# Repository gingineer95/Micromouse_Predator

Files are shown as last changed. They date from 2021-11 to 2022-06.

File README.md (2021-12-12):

Kailey Smith
# Mircomouse Predator from Scratch

## Project Overview

The goal of this project was to design, construct, and control a small wheeled robot, completely from scratch. Dr. Malcolm MacIver’s lab is studying robot-rodent interactions and required a robot to act as a high-speed predator that will constantly try to discover, chase, and corner a mouse in a maze-like habitat. 

To achieve this, I drew knowledge from my previous mechatronics experience to build a motor control circuit, communicate wirelessly using a Digi XBee module radio, as well as create a custom PCB. I also took inspiration from the <a href="https://en.wikipedia.org/wiki/Micromouse" target="_blank" rel="noopener noreferrer">Half-Sized Micromouse Competition</a> for both mechanical and electrical design. 

**The end result:** a remote controlled differential drive robot. Below is a video of robot being given left and right DC commands. It shows the robot moving forward and backwards, turning in a circle, and lastly moving in a loop. Note: these are only feed-forward commands, feed-back control is needed for precise movement.

Please checkout my [portfolio post](https://gingineer95.github.io/2021/12/11/micromouse/) for more details. 

forward_back

## Repo Hierarchy
MPLAB: Contains all C code, including programs used during breadboard testing and PCB testing.

Micromouse_solidworks_assembly: 3D modeled parts and assemblies.

Motor_Analysis: Contains a jupyter notebook in which I analyized different motors to use for the robot.

PCB_design: Contains all Eagle files, including libraries used and schematics/board desings

## Motor Analysis

My goal was to create a simulated “race” between a given brushed DC motor and the mice to find motors that ran faster than the mice. Dr. MaIver’s lab provided me with mouse trajectory and velocity data over time from their ongoing experiments. With this information to compare to, I needed to extrapolate equations to calculate a motor’s position and linear velocity over time given only a motor’s electrical specs. 

To model the motor’s behavior, I started using a simple equation that expresses input and outputs in terms of power below:

<p align="center">
\large {\color{White} IV = \tau \omega + {I}^2 R}   
</p>

Where *I* is the current through the motor, *V* is the voltage across the motor, \large {\color{White} \tau} and \large {\color{White} \omega} stand for torque and angular velocity on the output shaft and R is the motor’s internal resistance. The left side of the equation accounts for the electrical input power into a motor, while the right side accounts for the mechanical output power and power expelled through heat dissipation. After substituting in the torque constant {\color{White} k_t = \tau / I}, then {\color{White} \tau = mar} for torque, and {\color{White} \omega = v / r} for omega, I solved for an equation that is represented by the 1st and 2nd and 1st order differentials of displacement over time:

<p align="center">
\large {\color{White} a + \frac{v {k_t}^2}{Rm{r}^2} - \frac{V k_t}{Rmr} = 0} 
</p>

<p align="center">
\large {\color{White} \frac{d^2 x}{dt^2} + \frac{dx {k_t}^2}{Rm{r}^2 dt} - \frac{V k_t}{Rmr} = 0}
</p>

Once I had a function that was dependent on displacement over time, I was able to run the “race” simualtions. In order to get the robots linear and velocity displacement over time to compare to they mice, solved the equation for *x(t)* as well as *x'(t)*:

<p align="center">
\large {\color{White} x(t) = \frac{rV(k_t^2G^2 t + Rm{r}^2 ({e}^{-\frac{k_t^2G^2 t}{Rm{r}^2}} - 1))}{k_t^3G^3}}
</p>
<p align="center">
\large {\color{White} x'(t) = \frac{rV}{k_tG} (1 - {e}^{-\frac{k_t^2G^2 t}{Rm{r}^2}})}
</p>

Using the equations, I compared several motors to the mice by creating graphs such as the two below. The blue line represents the motor’s data while the green line represents a mouse.

mouse_race_data

I also examined each motor’s torque-speed curve to ensure that a motor’s anticipated torque outputs were within the continuous operating region of that motor. Using all graphs I was able to eliminate several motors while still having a couple of viable motors to choose from. 

My final motor selection came down to weight and size. For this entire system, the motors and battery we’re the largest and heaviest components. Therefore I wanted the smallest and lightest option of both. This meant choosing a 1 cell battery and therefore a motor that only needed up to 3.7V to operate. After doing some initial mechanical modeling, I chose a light and small motor that fit the design configuration I was looking for. 

## PCB Design

Once the critical parts were chosen, it was time to order all the other circuit components so I could start breadboarding and testing the circuit before ordering a custom PCB. I chose to use a PIC32 microcontroller since I had previous experience with these chips and there were a couple on hand to get started with quickly. Along those lines, I also chose to use the TI DRV8833 motor drivers. As a safety precaution, I added IR distance sensors to detect objects and avoid collisions. The last key component to this circuit was the Digi XBee 3 802.15.4 module which I used to communicate wirelessly with the robot. 

In order to integrate all the circuit components into a small area on the robot, a custom PCB was necessary. After I confirmed that my circuit worked on the breadboard, I had confidence that I could design a functional PCB. 

My initial thought was to use the PCB as a chassis component, as many of the Micromouse robots do. However, the MacIver lab uses a camera system above their habitat to track the mice and robot. And in order to detect, track, and determine the orientation of the robot, 3 red LEDs need to form an isosceles triangle on top of the robot. Given that, it was simple to rework the mechanical design so the PCB was the top-most component.

As with all PCB prototyping, this was a very iterative process, especially considering how many components needed to fit in such a small space. The dimensions of the PCB were determined by the footprint of the robot, which in turn was driven by the length of the motors. I was able to fit 35 components in a 46cm x 34cm space as pictured below.

<div align="center">View from OSHPark</div>

osh_park

Once the boards were manufactured, I soldered all the individual components myself using a microscope. I quickly realized I couldn’t program my microcontroller. I did a continuity test to identify the issue and discovered I didn’t have common ground across all the components. To get my PCB up and running as quickly as possible, I soldered jumper wires to all components that needed common ground. After that I was able to program the PIC and confirm that all my other connections were correct. I designed a new board with common ground for future use. 

<p align="center">

  board_wXB

</p>

## Mechanical Design

Below are images of the finalized, differential drive robot that I modeled in Soldiworks and then 3D printed.

<div align="center">Final design, 5cm wide by 5.5cm long</div>
<p align="center">

side1

iso1

</p>

I started with a four wheel configuration like many of the Micromouse designs. But after some testing, I discovered that the flooring in the MacIver lab habitat has a much higher coefficient of friction than the flooring used in the Micromouse competitions. I decided to remove two wheels and switch the tire material to a harder rubber o-ring which were skinner and therefore had smaller areas of contact to make turns easier. The thinner wheels also had the benefit of making the overall width of the robot smaller.

<p align="center">

  4wheel

2wheel
</p>

## Next Steps

As a safety feature the next immediate step will be incorporating the IR distance sensors as object avoidance / collision detection. I have already accounted for the sensors in my PCB, so all there is left to do is mount the hardware and implement functionality onto the microchip such that the robot stops if it senses that an object is too close. 

Given that there is a mechanically and electrically sound design, the next control steps are to add a PID controller. The MacIver lab is able to track the robot's location as it moves throughout the habitat. With that information, a position feedback controller can be implemented per the block diagram below. 

<p align="center">

pid_block

</p>

Once the PID controller is squared away, the final step for autonomous navigation will be to create a path planning algotihm. This algorithm will recevice a mouse location and plan a route from the robot's location to the mouse while avoiding all obstacles. With that, the predator robot will be fully operational!
Final Project for MSR program at Northwestern.

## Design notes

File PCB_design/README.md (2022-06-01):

Kailey Smith
# Mircomouse Predator from Scratch

## PCB Design

In this directory, I added my custom built library from EAGLE. There are several iterations of my PCB here, the version I'm currently using on the robot is v4, but this version does not have common ground. In the future, v6 should be used.

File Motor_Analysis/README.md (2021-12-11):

Kailey Smith
# Mircomouse Predator from Scratch

## Motor Analysis in Jupyter Notebook

This folder currently containts all the code I've used throughout this project. I'm in the process of commenting it, so please excuse the mess in the meantime. 

Whats important to note here are the Motor_Simulations_and_Torque-Speed_Graphs and Small_motor_analysis. These files are preactically idenitcal, the main difference being the first analysized several Maxon brand DC motors while the second analyzed small coreless pager motors.

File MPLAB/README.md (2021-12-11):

Kailey Smith
# Mircomouse Predator from Scratch

## C and MPLAB

This folder currently containts all the code I've used throughout this project. I'm in the process of commenting it, so please excuse the mess in the meantime. 

Whats important to note here are the 130_PCB_TEST and 170_PCB_TEST projects made in MPLAB. For this project I had to use two different PICs due to confilcts in my original design and chip availibilty during COVID (PIC32MX**130**F256B and PIC32MX**170**F256B). The functionality of both code is the same, I just had to program the same code twice for the different PICs.

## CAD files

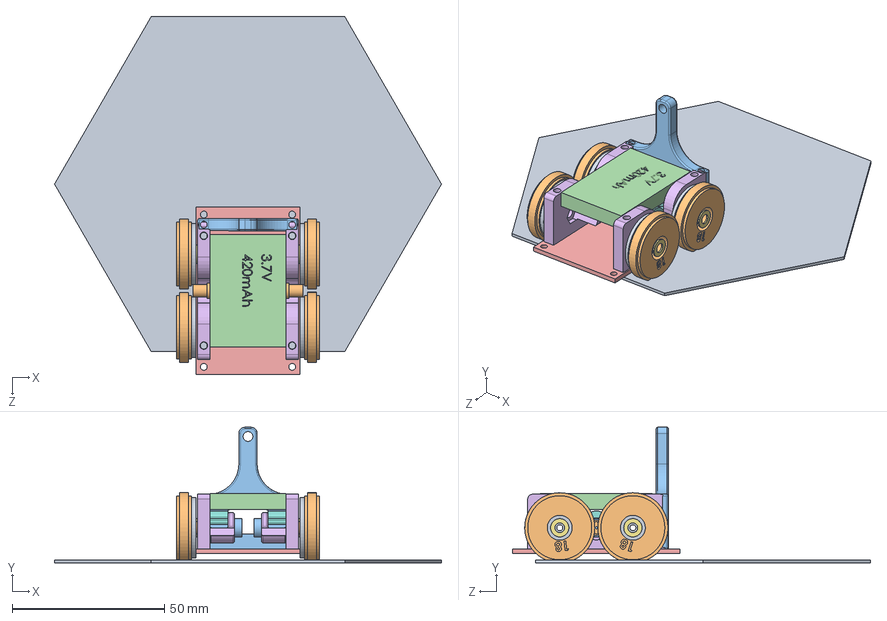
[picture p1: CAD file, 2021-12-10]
Micromouse_solidworks_assembly/MK06-45_assembly.SLDASM
127.0 x 44.5 x 117.5 mm
hex
23OD_wheel_18ID_oring x 4
MK06-45 x 2
37V_420_ada_battery
PCB_v2
motor_mount_bot_v5 x 2
M3_washer x 8
Motor_mount_top x 2
38T2A x 4
8tooth_08A x 2
IR_front_back_mount

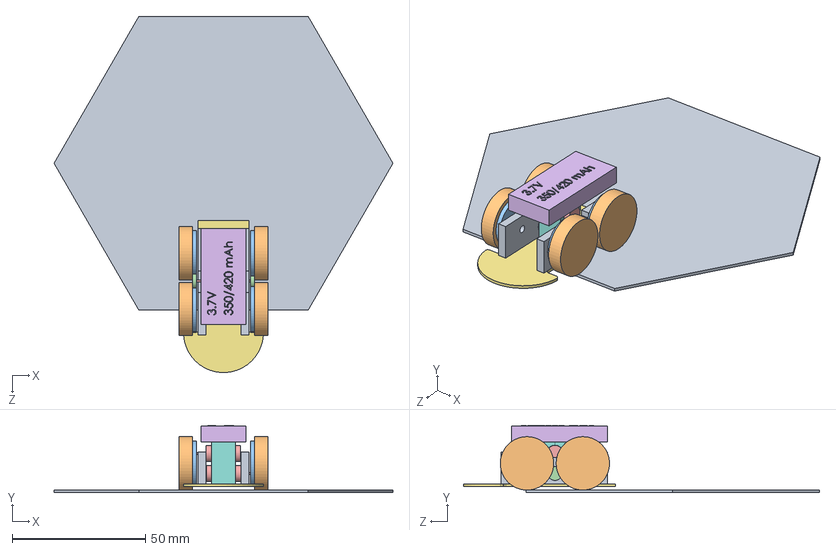
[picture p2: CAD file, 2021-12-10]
Micromouse_solidworks_assembly/MK06-45_stacked_assembly.SLDASM
127.0 x 25.3 x 133.4 mm
hex
2cm_wheel x 4
32tooth_gear_48 x 4
10tooth_gear_48 x 2
MK06-45 x 2
37V_350_420_battery
PCB_MK06_v2
MK06_v2_motor_mount x 2
MK06_v2_wheel_mount x 2

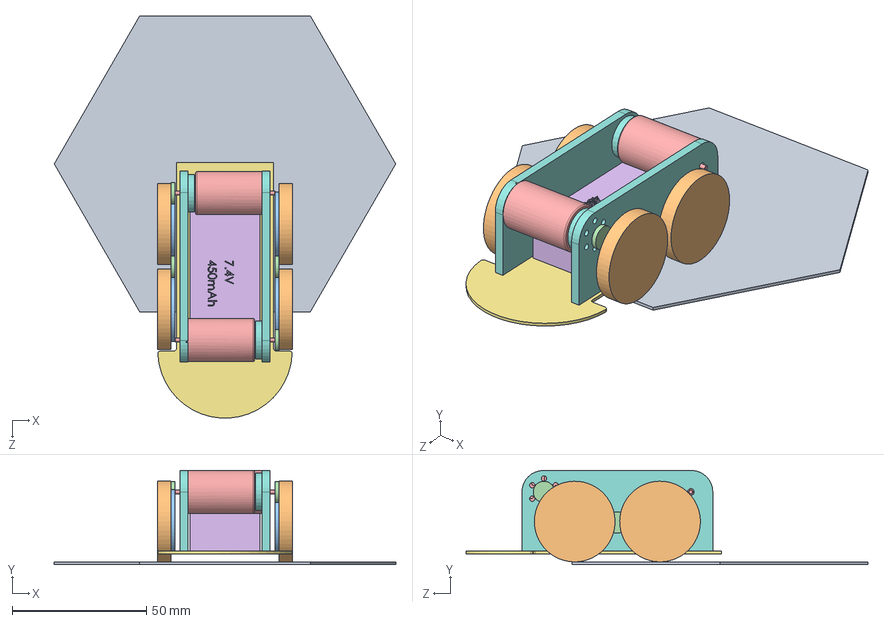
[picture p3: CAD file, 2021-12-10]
Micromouse_solidworks_assembly/DC_max_16S_assembly.SLDASM
127.0 x 35.0 x 149.5 mm
hex
3cm_wheel x 4
30tooth_gear_32 x 4
10tooth_gear_32 x 4
DC_max_16S x 2
7V_450_battery
PCB_16S
16S_motor_mount x 2

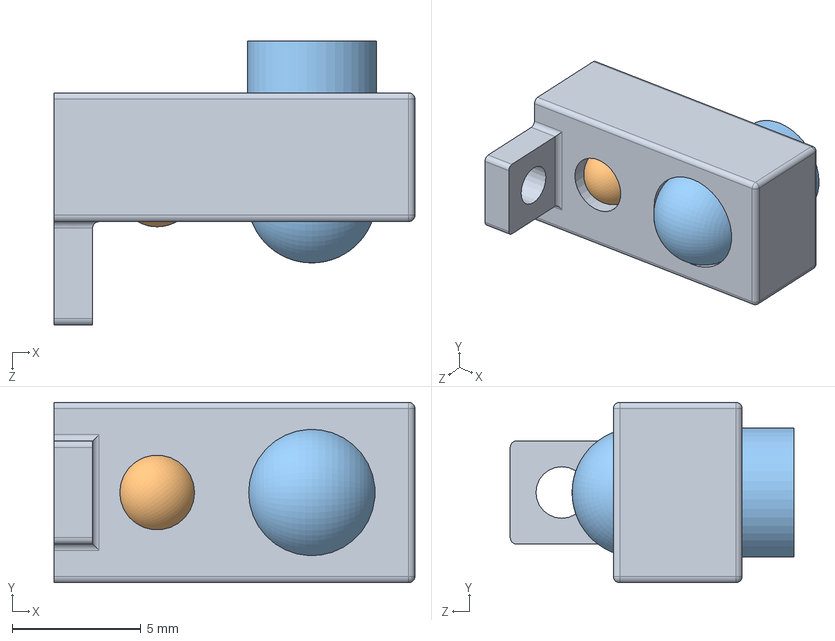
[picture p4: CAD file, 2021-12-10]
Micromouse_solidworks_assembly/IR_combo.SLDASM
14.0 x 7.00 x 11.0 mm
IR_mount
IR_reciver
IR_emmiter

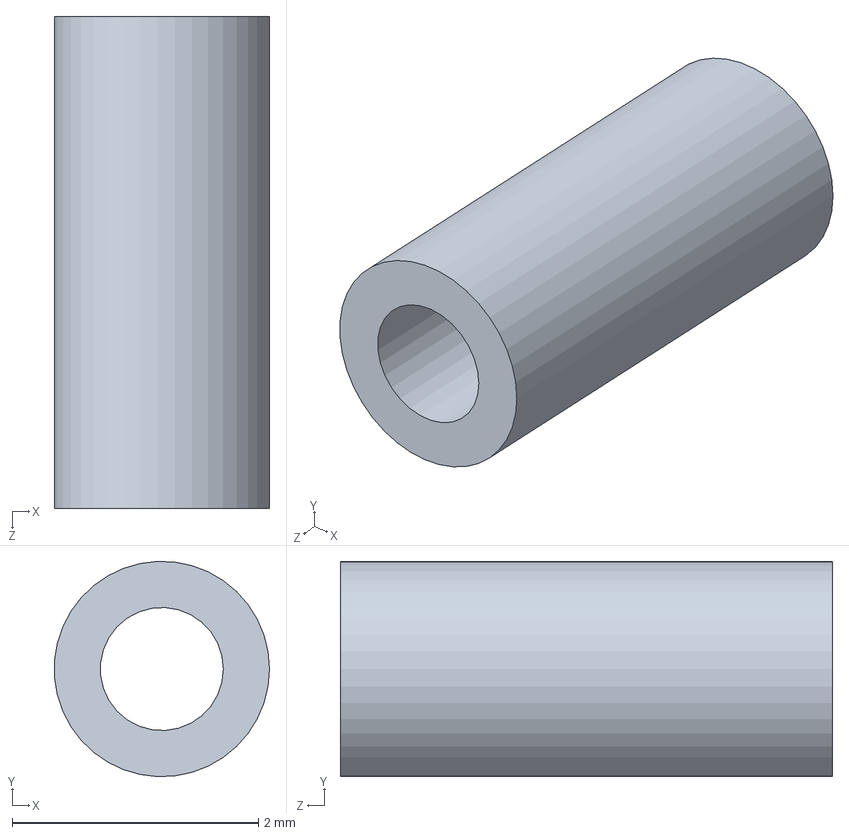
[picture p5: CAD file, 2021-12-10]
Micromouse_solidworks_assembly/1.75mmOD_4mmL_motor_shaft.SLDPRT
1.75 x 1.75 x 4.00 mm

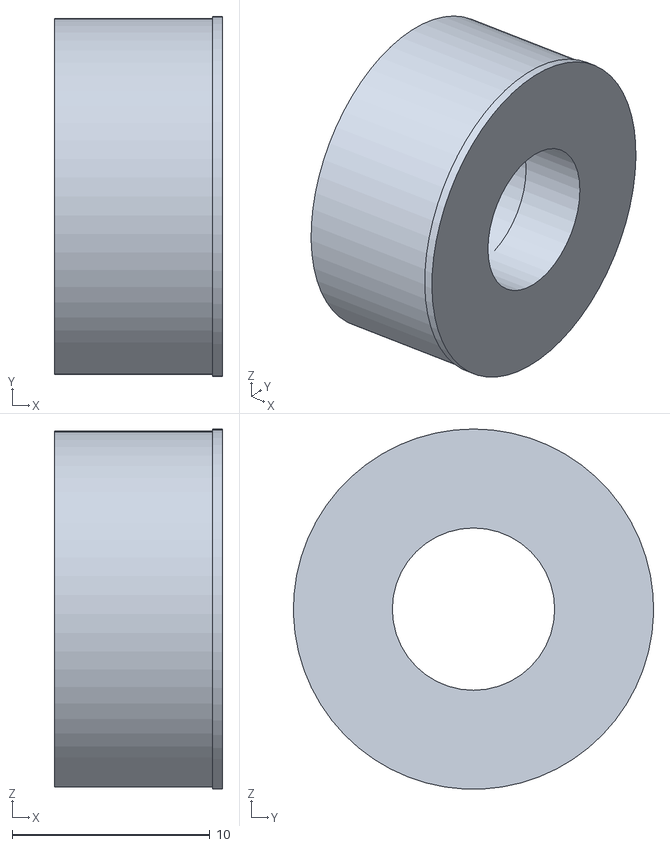
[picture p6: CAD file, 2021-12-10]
Micromouse_solidworks_assembly/STLs/25mm_91_85_kysho_wheel.STL
8.50 x 18.2 x 18.2

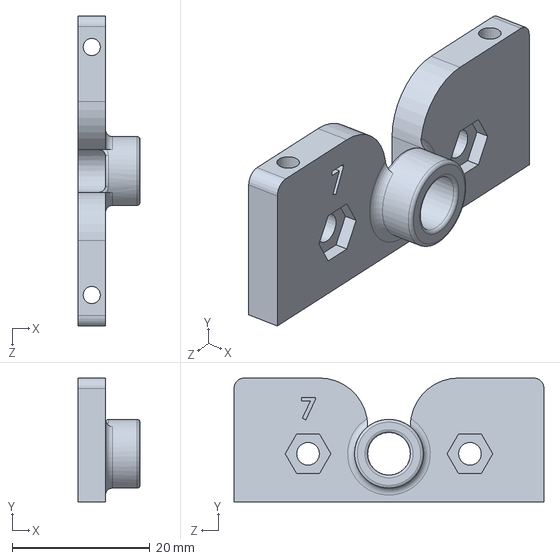
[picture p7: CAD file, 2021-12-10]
Micromouse_solidworks_assembly/motor_mount_bot_v7.SLDPRT
9.00 x 18.0 x 45.0 mm

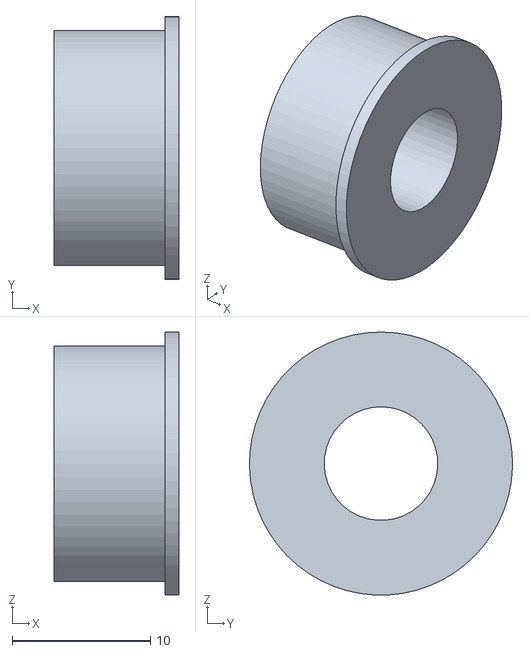
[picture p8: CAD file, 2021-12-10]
Micromouse_solidworks_assembly/STLs/R92mm_9mm_wd_kysho_wheel.STL
9.00 x 19.0 x 19.0

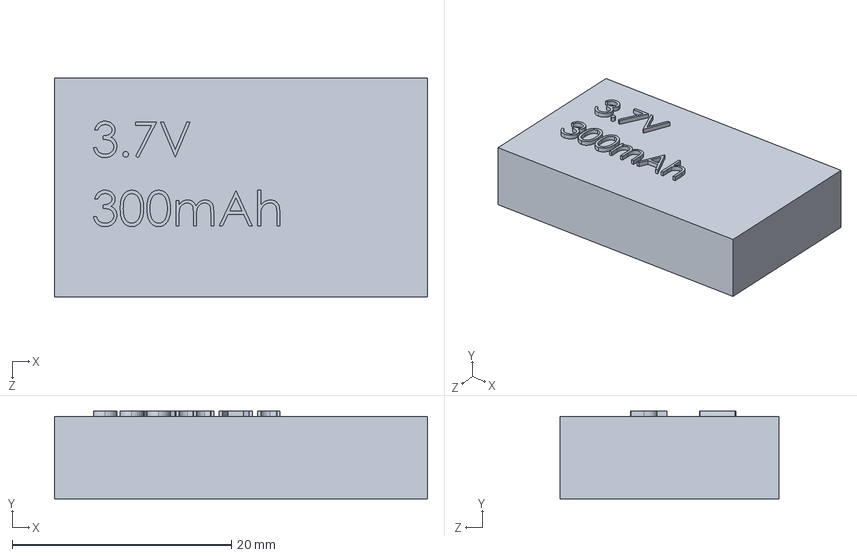
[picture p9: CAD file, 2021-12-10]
Micromouse_solidworks_assembly/37V_300_battery.SLDPRT
34.0 x 8.00 x 20.0 mm

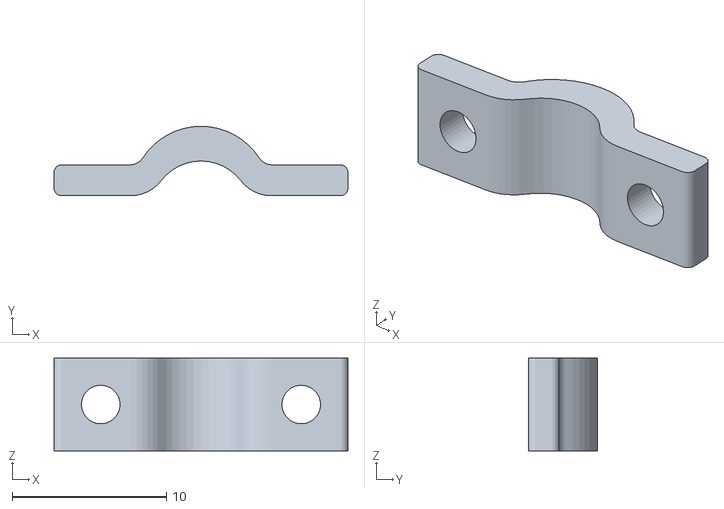
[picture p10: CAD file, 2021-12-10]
Micromouse_solidworks_assembly/STLs/Motor_mount_top_v4.STL
19.1 x 4.50 x 6.00

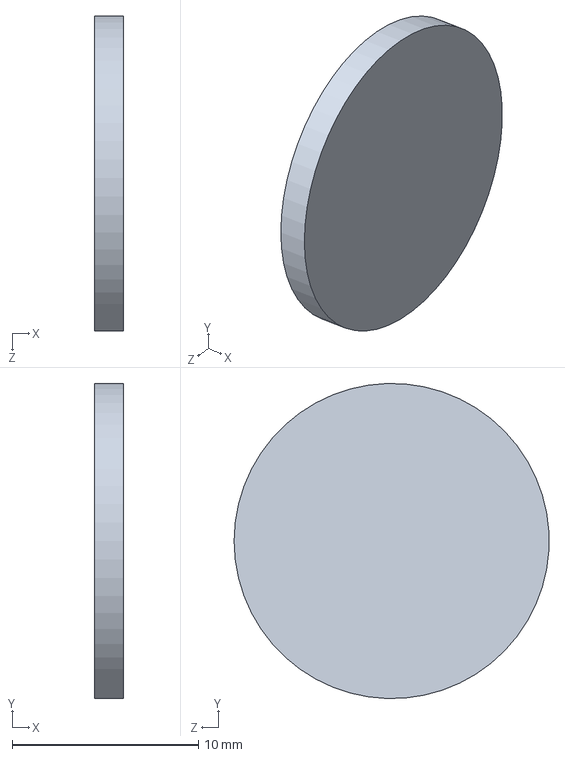
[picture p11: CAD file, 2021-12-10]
Micromouse_solidworks_assembly/32tooth_gear_48.SLDPRT
1.57 x 16.9 x 16.9 mm

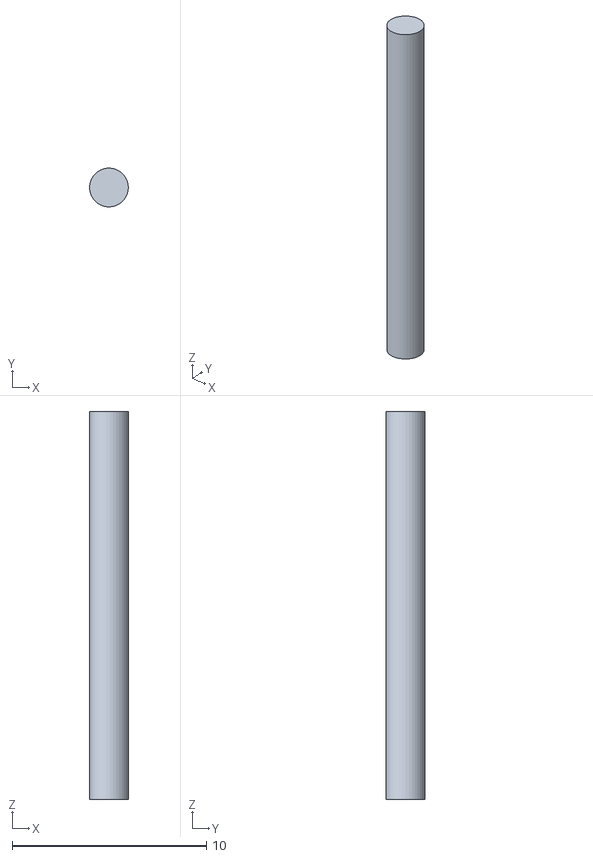
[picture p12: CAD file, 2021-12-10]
Micromouse_solidworks_assembly/STLs/wheel_rod.STL
2.00 x 2.00 x 20.0

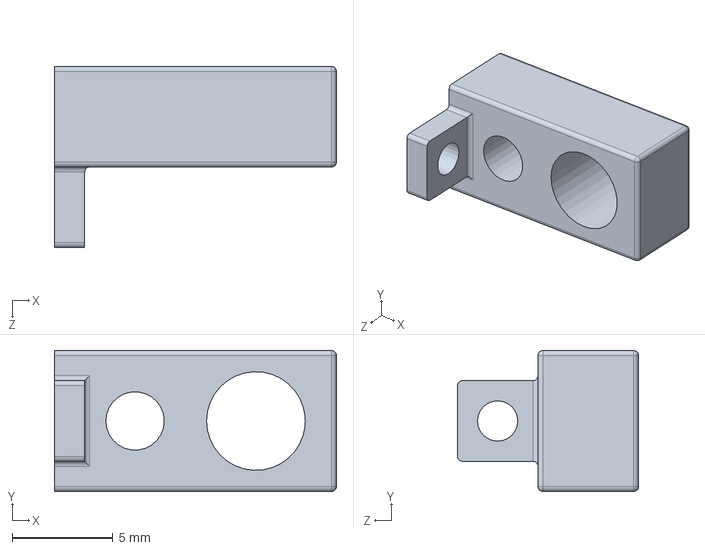
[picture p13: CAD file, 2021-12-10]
Micromouse_solidworks_assembly/IR_mount.SLDPRT
14.0 x 7.00 x 9.00 mm

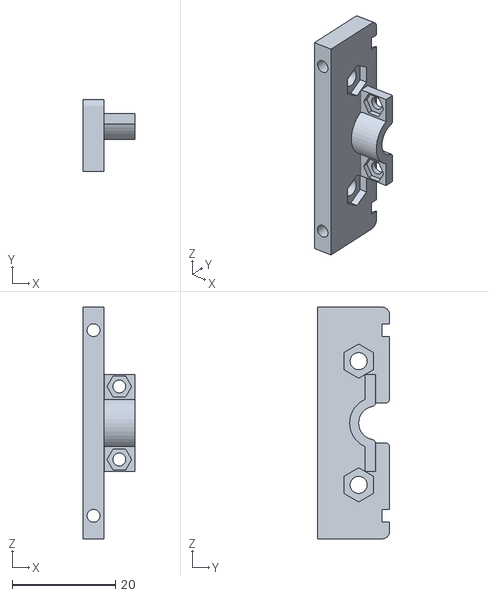
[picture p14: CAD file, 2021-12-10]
Micromouse_solidworks_assembly/STLs/MK06_motor_mount_bottom.STL
10.0 x 14.0 x 45.0

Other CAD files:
Micromouse_solidworks_assembly/PCB_16S.SLDPRT
Micromouse_solidworks_assembly/STLs/PCB_v2_2.STL
Micromouse_solidworks_assembly/hex.SLDPRT
Micromouse_solidworks_assembly/STLs/motor_mount_bot_v3_25cm.STL
Micromouse_solidworks_assembly/10tooth_gear_32.SLDPRT
Micromouse_solidworks_assembly/10tooth_gear_48.SLDPRT
Micromouse_solidworks_assembly/16S_motor_mount.SLDPRT
Micromouse_solidworks_assembly/20cm_wheel.SLDPRT
Micromouse_solidworks_assembly/20mm_wheel_oring.SLDPRT
Micromouse_solidworks_assembly/21OD_wheel_16ID_oring.SLDPRT
Micromouse_solidworks_assembly/22OD_wheel_17ID_oring.SLDPRT
Micromouse_solidworks_assembly/23OD_wheel_18ID_oring.SLDPRT
Micromouse_solidworks_assembly/25cm_wheel.SLDPRT
Micromouse_solidworks_assembly/25mm_kysho_wheel.SLDPRT
Micromouse_solidworks_assembly/25mm_test_wheel.SLDPRT
Micromouse_solidworks_assembly/25mm_wheel_oring.SLDPRT
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

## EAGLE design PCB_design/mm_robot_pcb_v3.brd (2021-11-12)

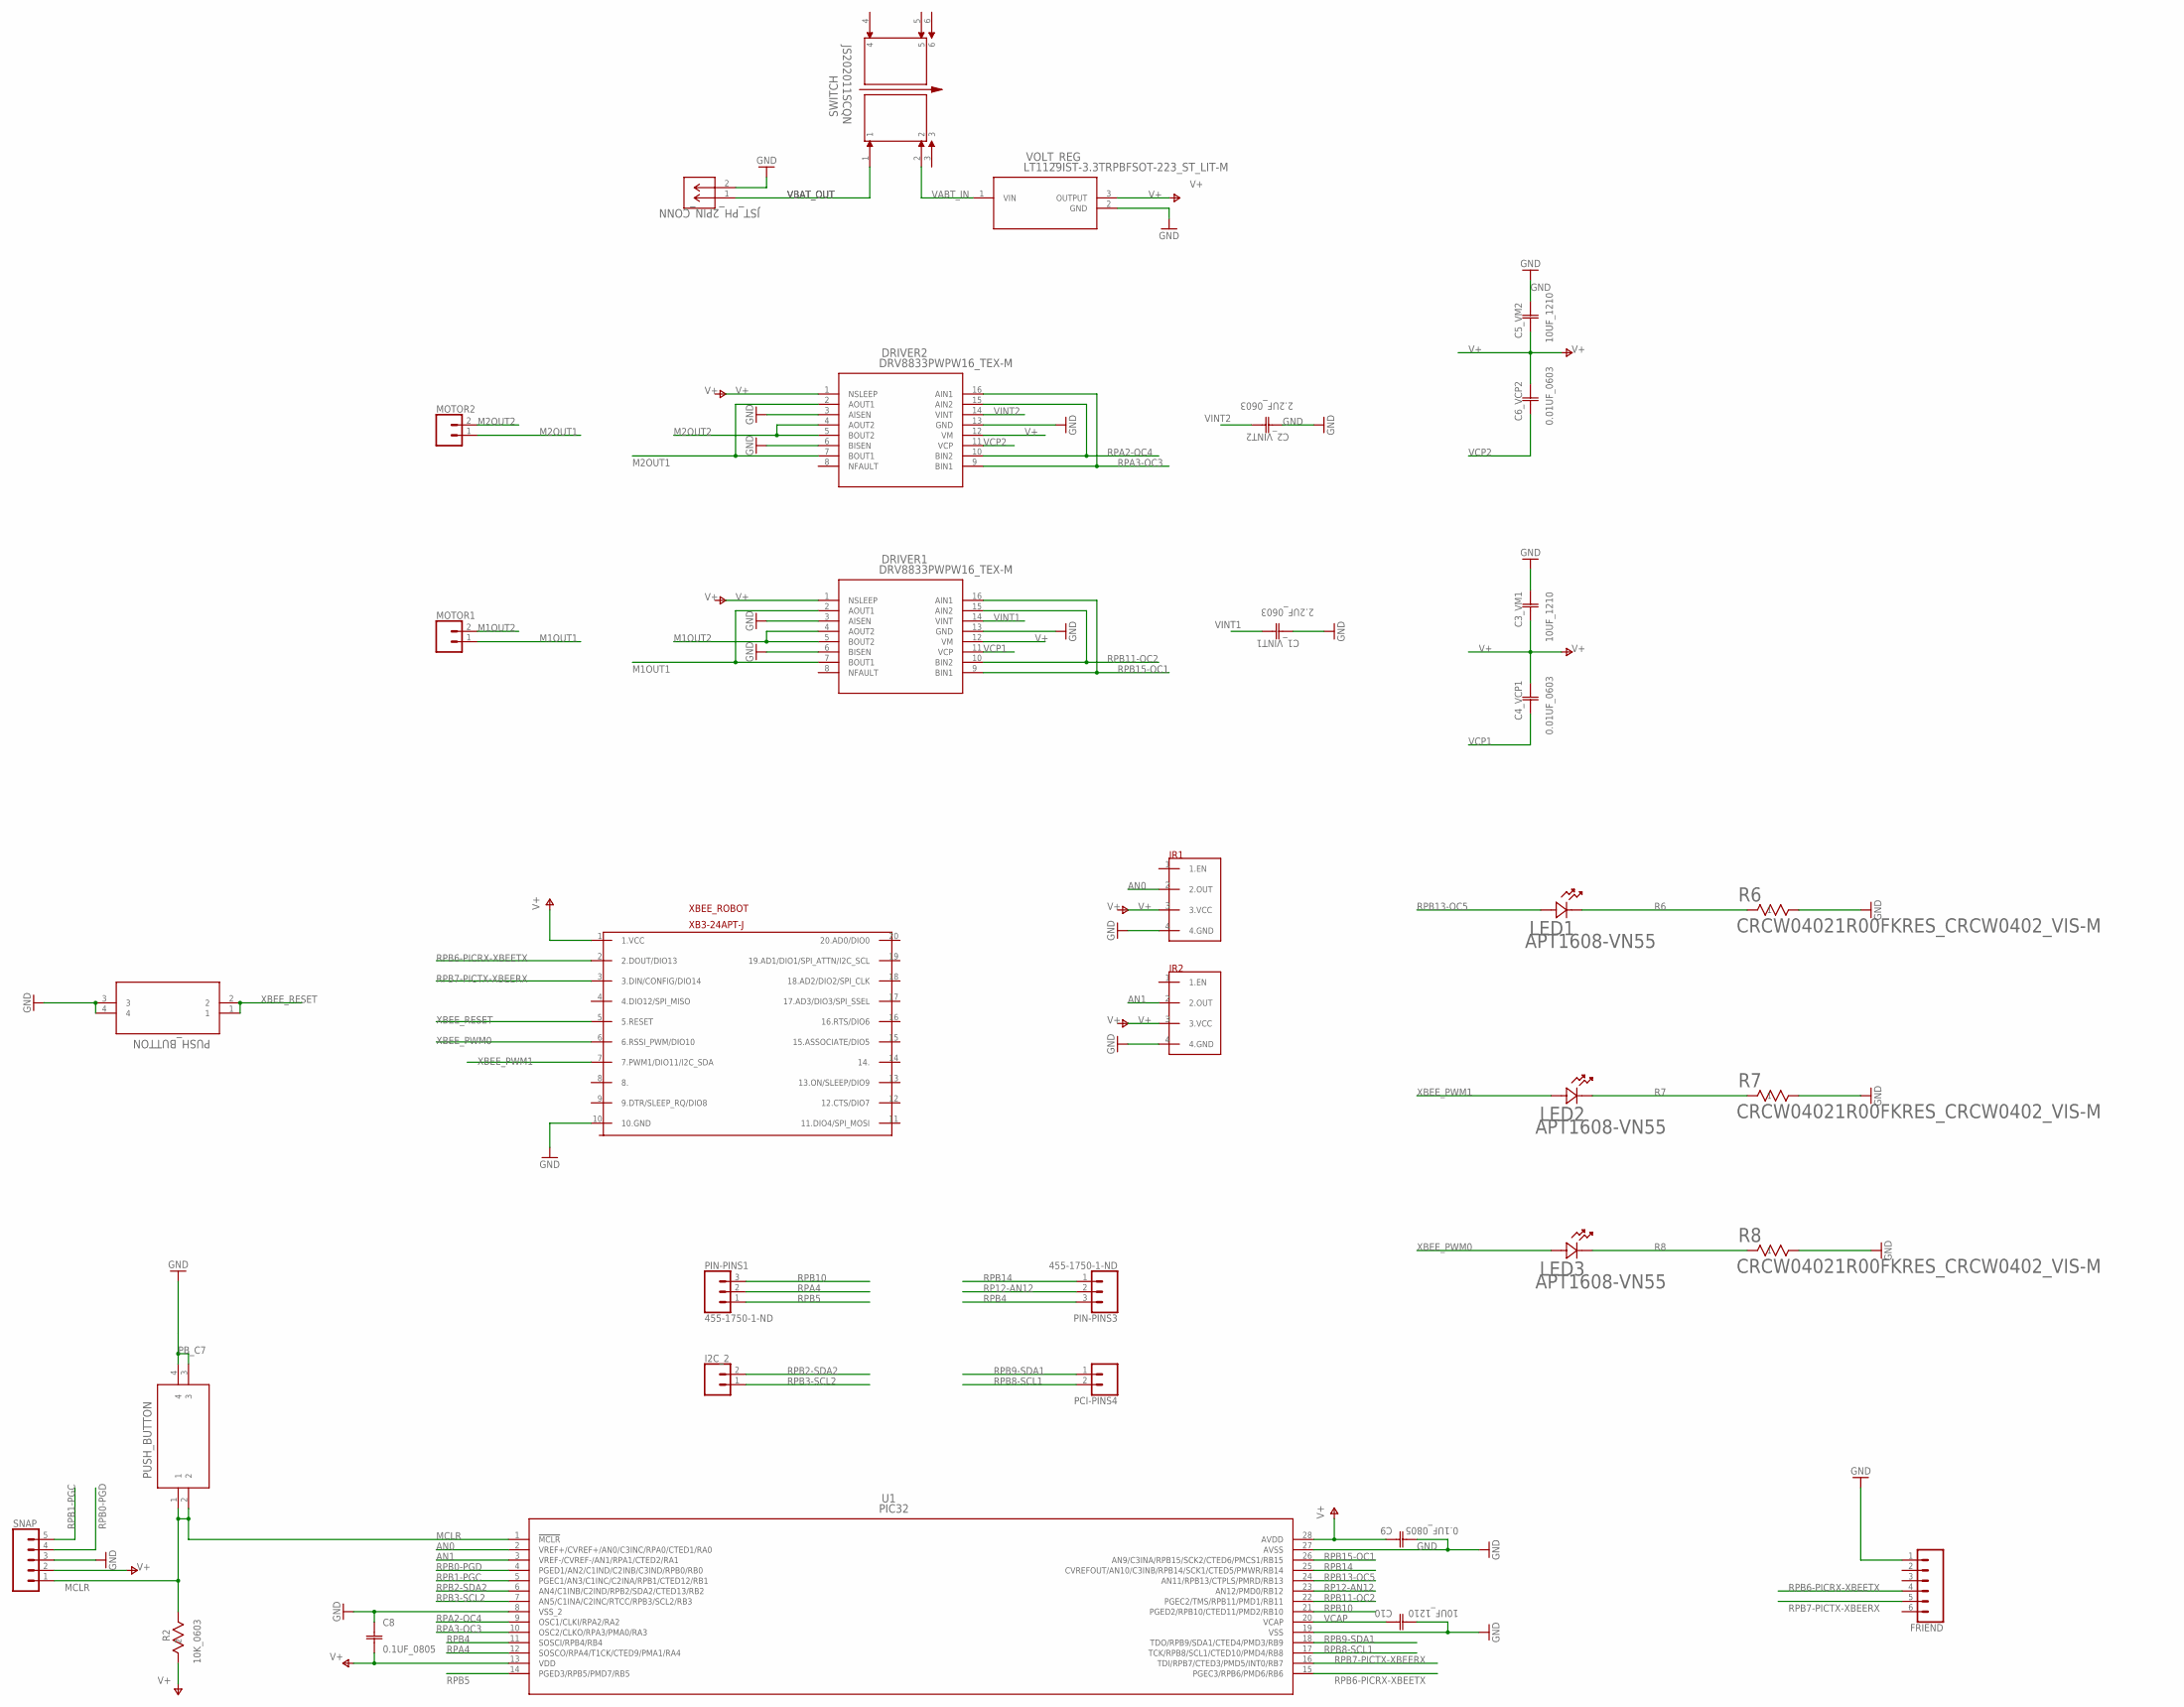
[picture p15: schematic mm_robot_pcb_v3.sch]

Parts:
C1_VINT1, C2_VINT2: 2.2UF_0603; CAP_CL10_SAM-M
C3_VM1, C5_VM2, C10: 10UF_1210; CAP_TPS_B_AVX-M
C4_VCP1, C6_VCP2: 0.01UF_0603; CAP_01UF_0603_X7R_G_AVX
C8, C9: 0.1UF_0805; CAP_C2012X7R2A104K125AA_TDK-M
DRIVER1, DRIVER2: DRV8833PWPW16_TEX-M; PW16_TEX-M
FRIEND: CONN_06NO_SILK_FEMALE_PTH; 1X06_NO_SILK
I2C_2: CONN_02; 1X02
IR1, IR2: GP2Y0A60SZLF; 1X04
JST_PH_2PIN_CONN: 1769; CONN_1769_ADA
LED1, LED2, LED3: APT1608-VN55; LED_APT1608_KNB
MOTOR1, MOTOR2: CONN_02; 1X02
PCI-PINS4: CONN_02; 1X02
PIC_PB: PUSH_BUTTON; SMT_FS-M
PIN-PINS1, PIN-PINS3: 455-1750-1-ND; 1X03
R2: 10K_0603; RES0603_CRG_TYCO_TYC-M
R6, R7, R8: CRCW04021R00FKRES_CRCW0402_VIS-M; RES_CRCW0402_VIS-M
SNAP: CONN_05; 1X05
SWITCH: JS202011SCQN; SW_JS202011SCQN
U1: PIC32; SSOP28_MC_MCH-M
VOLT_REG: LT1129IST-3.3TRPBFSOT-223_ST_LIT-M; SOT-223_ST_LIT-M
XBEE_PB: PUSH_BUTTON; SMT_FS-M
XBEE_ROBOT: XB3-24APT-J

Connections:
AN0: IR1.2 (2.OUT), U1.2 (VREF+/CVREF+/AN0/C3INC/RPA0/CTED1/RA0)
AN1: IR2.2 (2.OUT), U1.3 (VREF-/CVREF-/AN1/RPA1/CTED2/RA1)
GND: C1_VINT1.1, C2_VINT2.1, C3_VM1.2 (12), C5_VM2.2 (12), C8.1, C9.1, C10.1 (11), DRIVER1.3 (AISEN), DRIVER1.6 (BISEN), DRIVER1.13 (GND), DRIVER2.3 (AISEN), DRIVER2.6 (BISEN), DRIVER2.13 (GND), FRIEND.1, IR1.4 (4.GND), IR2.4 (4.GND), JST_PH_2PIN_CONN.2, R6.2, R7.2, R8.2, SNAP.3, U1.8 (VSS_2), U1.19 (VSS), U1.27 (AVSS), VOLT_REG.2 (GND), XBEE_PB.3, XBEE_PB.4, XBEE_ROBOT.10 (10.GND)
M1OUT1: DRIVER1.2 (AOUT1), DRIVER1.7 (BOUT1), MOTOR1.1
M1OUT2: DRIVER1.4 (AOUT2), DRIVER1.5 (BOUT2), MOTOR1.2
M2OUT1: DRIVER2.2 (AOUT1), DRIVER2.7 (BOUT1), MOTOR2.1
M2OUT2: DRIVER2.4 (AOUT2), DRIVER2.5 (BOUT2), MOTOR2.2
MCLR: PIC_PB.1, PIC_PB.2, R2.1, SNAP.1, U1.1 (!MCLR)
PB_C7: PIC_PB.3, PIC_PB.4
R6: LED1.1, R6.1
R7: LED2.1, R7.1
R8: LED3.1, R8.1
RP12-AN12: PIN-PINS3.2, U1.23 (AN12/PMD0/RB12)
RPA2-OC4: DRIVER2.10 (BIN2), DRIVER2.15 (AIN2), U1.9 (OSC1/CLKI/RPA2/RA2)
RPA3-OC3: DRIVER2.9 (BIN1), DRIVER2.16 (AIN1), U1.10 (OSC2/CLKO/RPA3/PMA0/RA3)
RPA4: PIN-PINS1.2, U1.12 (SOSCO/RPA4/T1CK/CTED9/PMA1/RA4)
RPB0-PGD: SNAP.4, U1.4 (PGED1/AN2/C1IND/C2INB/C3IND/RPB0/RB0)
RPB1-PGC: SNAP.5, U1.5 (PGEC1/AN3/C1INC/C2INA/RPB1/CTED12/RB1)
RPB2-SDA2: I2C_2.2, U1.6 (AN4/C1INB/C2IND/RPB2/SDA2/CTED13/RB2)
RPB3-SCL2: I2C_2.1, U1.7 (AN5/C1INA/C2INC/RTCC/RPB3/SCL2/RB3)
RPB4: PIN-PINS3.3, U1.11 (SOSCI/RPB4/RB4)
RPB5: PIN-PINS1.1, U1.14 (PGED3/RPB5/PMD7/RB5)
RPB6-PICRX-XBEETX: FRIEND.4, U1.15 (PGEC3/RPB6/PMD6/RB6), XBEE_ROBOT.2 (2.DOUT/DIO13)
RPB7-PICTX-XBEERX: FRIEND.5, U1.16 (TDI/RPB7/CTED3/PMD5/INT0/RB7), XBEE_ROBOT.3 (3.DIN/CONFIG/DIO14)
RPB8-SCL1: PCI-PINS4.2, U1.17 (TCK/RPB8/SCL1/CTED10/PMD4/RB8)
RPB9-SDA1: PCI-PINS4.1, U1.18 (TDO/RPB9/SDA1/CTED4/PMD3/RB9)
RPB10: PIN-PINS1.3, U1.21 (PGED2/RPB10/CTED11/PMD2/RB10)
RPB11-OC2: DRIVER1.10 (BIN2), DRIVER1.15 (AIN2), U1.22 (PGEC2/TMS/RPB11/PMD1/RB11)
RPB13-OC5: LED1.2, U1.24 (AN11/RPB13/CTPLS/PMRD/RB13)
RPB14: PIN-PINS3.1, U1.25 (CVREFOUT/AN10/C3INB/RPB14/SCK1/CTED5/PM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)
RPB15-OC1: DRIVER1.9 (BIN1), DRIVER1.16 (AIN1), U1.26 (AN9/C3INA/RPB15/SCK2/CTED6/PMCS1/RB15)
V+: C3_VM1.1 (11), C4_VCP1.2, C5_VM2.1 (11), C6_VCP2.2, C8.2, C9.2, DRIVER1.1 (NSLEEP), DRIVER1.12 (VM), DRIVER2.1 (NSLEEP), DRIVER2.12 (VM), IR1.3 (3.VCC), IR2.3 (3.VCC), R2.2, SNAP.2, U1.13 (VDD), U1.28 (AVDD), VOLT_REG.3 (OUTPUT), XBEE_ROBOT.1 (1.VCC)
VABT_IN: SWITCH.2, VOLT_REG.1 (VIN)
VBAT_OUT: JST_PH_2PIN_CONN.1, SWITCH.1
VCAP: C10.2 (12), U1.20 (VCAP)
VCP1: C4_VCP1.1, DRIVER1.11 (VCP)
VCP2: C6_VCP2.1, DRIVER2.11 (VCP)
VINT1: C1_VINT1.2, DRIVER1.14 (VINT)
VINT2: C2_VINT2.2, DRIVER2.14 (VINT)
XBEE_PWM0: LED3.2, XBEE_ROBOT.6 (6.RSSI_PWM/DIO10)
XBEE_PWM1: LED2.2, XBEE_ROBOT.7 (7.PWM1/DIO11/I2C_SDA)
XBEE_RESET: XBEE_PB.1, XBEE_PB.2, XBEE_ROBOT.5 (5.RESET)

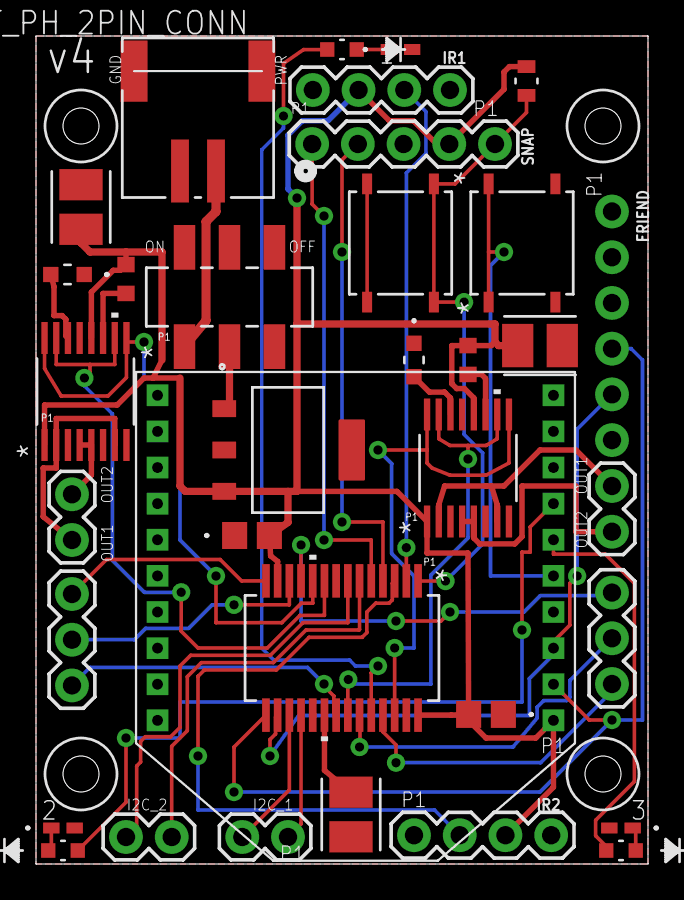
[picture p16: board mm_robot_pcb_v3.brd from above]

Board: 2 copper layers, 34.0 x 46.0 mm, 35 parts (0 on the bottom side), 42 nets.

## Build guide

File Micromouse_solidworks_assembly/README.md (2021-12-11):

Kailey Smith
# Mircomouse Predator from Scratch

## SOLIDWORKS / 3D modeling

This folder currently containts all the models I've created / used throughout this project. I'm in the process of orgqnizing it, so please excuse the mess in the meantime. 

The current robot's assmebly model is MK06-45_assembly. Please refer to this assmebly when looking for the most up to date components.

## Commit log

2021-05-18 Working on my simulations. I'm able to elimate motors that cant meet the power requirements, now I need to look at different gear ratios and how those affect the trajectories
2021-05-19 Updated my motor selection notebook with a reccomendation of the DCX12L
2021-05-21 Completed motor analysis based on mouse data and made motor reccomendations
    [1.5W_motors_v2.csv, 2.5W_motors_v2.csv, 2W_motors_v2.csv, 3W_motors_v2.csv]
2021-05-26 Updated analysis with gear and battery calculations
2021-06-02 Added some analysis for the smaller Micromouse motors
2021-06-02 Updated my tiny motor analysis
2021-06-08 Added updated library and also a schematic for the motor driving ciruit
    [Motor_circuit.sch]
2021-11-12 Re-organized directory. Added Eagle boards and schematics for my PCB user the folder 'PCB_design'. Added all C code written until now under 'MPLAB'. Moved all previous motor analysis files under 'Mot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
    [1.5W_motors_v2.csv, 2.5W_motors_v2.csv, 2W_motors_v2.csv, 3W_motors_v2.csv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]
2021-12-10 Added all soldiworks models
    [1.75mmOD_4mmL_motor_shaft.SLDPRT, 1.75mmOD_4mmL_motor_shaft.STL, 10tooth_gear_32.SLDPRT, 10tooth_gear_48.SLDPRT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]
2022-06-01 Renamed PCB files so they're numbered correctly
    [mm_robot_pcb_v3.brd, mm_robot_pcb_v3.sch, mm_robot_pcb_v4.brd, mm_robot_pcb_v4.sch]

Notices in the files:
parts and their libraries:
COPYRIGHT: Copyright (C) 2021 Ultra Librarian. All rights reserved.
